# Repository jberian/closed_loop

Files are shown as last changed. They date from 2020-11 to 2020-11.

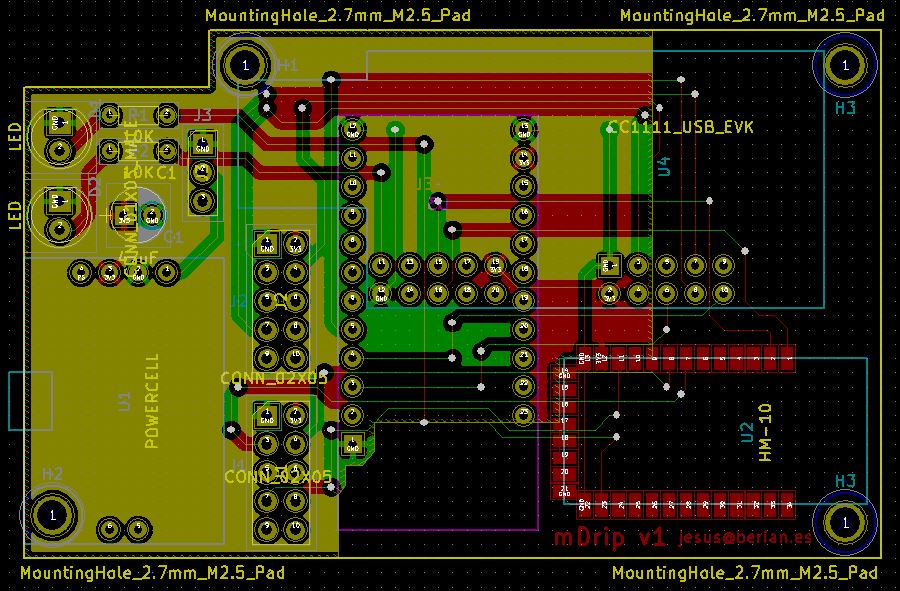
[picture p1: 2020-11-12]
Platform/Prototype/mDrip-BB.JPG

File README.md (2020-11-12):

Closed-Loop System for Type 1 diabetes
====

    This repository contains all the projects needed to build a 
    wearable closed-loop system for type 1 diabetes that uses a new
    algorithm to estimate the basal insulin needs of the patient and
    perform the control using temporary basal rates.

## Disclaimer

    This software and information is designed for educational purposes only 
    and should NEVER be used on real patients.
    
    This information is provided 'as is' and in no event shall the 
    provider be liable for any damages, including, without 
    limitation, damages resulting from lost data or lost profits or 
    revenue, the costs of recovering such data, the costs of substitute 
    data, claims by third parties or for other similar costs, or any 
    special, incidental, or consequential damages arising out of use or
    misuse of this data. The accuracy or reliability of the data is not 
    guaranteed or warranted in any way and the provider disclaim 
    liability of any kind whatsoever, including, without limitation, 
    liability for quality, performance, merchantability and fitness 
    for a particular purpose arising out of the use, or inability 
    to use the data. Information obtained via this software MUST
    NEVER BE USED to take medical decisions.

## [License - GPL V2](gpl-v2)
[gpl-2]: https://www.gnu.org/licenses/old-licenses/gpl-2.0.txt

    This program is free software: you can redistribute it and/or modify
    it under the terms of the GNU General Public License as published by
    the Free Software Foundation version 2 of the License.

    This program is distributed in the hope that it will be useful,
    but WITHOUT ANY WARRANTY; without even the implied warranty of
    MERCHANTABILITY or FITNESS FOR A PARTICULAR PURPOSE.  See the
    GNU General Public License for more details.

    You should have received a copy of the GNU General Public License
    along with this program.  If not, see <http://www.gnu.org/licenses/>.

## Contents

   This repository containts the following information in their corresponding
   folder:
   
1. **Demo** - Contains a time-lapse video of a demo system connected to Nightscout and controlling a patient's glycaemia.

2. **Firmware** - Contains the project files needed to compile the platform's CC1111 firmware using IAR Embedded Workbench (the trial version should be enough). The code for the CC2540 processor is not included since the project should be downloaded directly from TI's website.
   
3. **Platform** - Contains the information to build two different platforms: 
    1. *Prototype* - It's a PCB in which some commercial off-the-self boards can be soldered and provides the needed interconnections for the system.
    2. *Final* - Final version of the wearable system.
 
4. **Publications** - Publications related to this work.

5. **Simulation** - Contains a modified version of the [simglucose simulator](https://github.com/jxx123/simglucose) along with a controller that behaves like the "real" version of the controller.

6. **Uploader** - Contains the xCode project for an really simple iOS uploader for Nightscout. This software allows the platform to upload data to Nightscout using an iOS device.

## Thanks

None of this would be possible without all the hard work of my colleagues Ignacio Bravo, Alfredo Gardel and Jose Luis Lazaro.

Sergio Hernandez, thank you very much for your countless hours of hardware designing.

And thank you Jinyu Xie for developing such excellent software ([simglucose](https://github.com/jxx123/simglucose)) and allow us to build upon it.

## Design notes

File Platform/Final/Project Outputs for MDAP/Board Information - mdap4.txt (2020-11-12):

Board Information Report
Filename     : D:\data\work\mdap\Altium\MDAP\mdap4.PcbDoc
Date         : 19/02/2015
Time         : 20:14:05
Time Elapsed : 00:00:00

Routing Information
    Routing completion, 100,00%
    Connections, 347
    Connections routed, 347
    Connections remaining, 0
count : 4

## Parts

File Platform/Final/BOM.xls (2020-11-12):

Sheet: Hoja1
 |  |  | farnell |  |  |  |  |  | rs |  | pn |  |  | Prec.unit
Part | cc2510.SchDoc | A200 |  | * | * | * | * | * |  | * | * | * | * | 0
Part | CC2540.SchDoc | A300 |  | * | * | * | * | * |  | * | * | * | * | 0
Part | cc1110.SchDoc | C100 | 2426879 | Re-released for DXP Platform. | Radial Cap, Thru-Hole; 2 Leads; 0.3 in Pin Spacing | RAD-0.3 | 2000-06-08 | Altium Limited | 624-2941 | 220pF | * | * | * | 0.0338
Part | cc1110.SchDoc | C101 | 2426879 | Re-released for DXP Platform. | Radial Cap, Thru-Hole; 2 Leads; 0.3 in Pin Spacing | RAD-0.3 | 2000-06-08 | Altium Limited | 624-2941 | 220pF | * | * | * | 0.0338
Part | cc1110.SchDoc | C102 | 1865457 | Re-released for DXP Platform. | Radial Cap, Thru-Hole; 2 Leads; 0.3 in Pin Spacing | RAD-0.3 | 2000-06-08 | Altium Limited | 788-2843 | 100nF | * | * | * | 0.0126
Part | cc1110.SchDoc | C103 | 1865457 | Re-released for DXP Platform. | Radial Cap, Thru-Hole; 2 Leads; 0.3 in Pin Spacing | RAD-0.3 | 2000-06-08 | Altium Limited | 788-2843 | 100nF | * | * | * | 0.0126
Part | cc1110.SchDoc | C104 | 1865457 | Re-released for DXP Platform. | Radial Cap, Thru-Hole; 2 Leads; 0.3 in Pin Spacing | RAD-0.3 | 2000-06-08 | Altium Limited | 788-2843 | 100nF | * | * | * | 0.0126
Part | cc1110.SchDoc | C105 | 1865457 | Re-released for DXP Platform. | Radial Cap, Thru-Hole; 2 Leads; 0.3 in Pin Spacing | RAD-0.3 | 2000-06-08 | Altium Limited | 788-2843 | 100nF | * | * | * | 0.0126
Part | cc1110.SchDoc | C106 | 2426879 | Re-released for DXP Platform. | Radial Cap, Thru-Hole; 2 Leads; 0.3 in Pin Spacing | RAD-0.3 | 2000-06-08 | Altium Limited | 749-2138 | 2u2 | * | * | * | 0.0338
Part | cc1110.SchDoc | C107 | 1865457 | Re-released for DXP Platform. | Radial Cap, Thru-Hole; 2 Leads; 0.3 in Pin Spacing | RAD-0.3 | 2000-06-08 | Altium Limited | 788-2843 | 100nF | * | * | * | 0.0126
Part | cc1110.SchDoc | C108 | 2426879 | Re-released for DXP Platform. | Radial Cap, Thru-Hole; 2 Leads; 0.3 in Pin Spacing | RAD-0.3 | 2000-06-08 | Altium Limited | 749-2138 | 2u2 | * | * | * | 0.0338
Part | cc1110.SchDoc | C109 | 1865457 | Re-released for DXP Platform. | Radial Cap, Thru-Hole; 2 Leads; 0.3 in Pin Spacing | RAD-0.3 | 2000-06-08 | Altium Limited | 806-8495 | 100pF | * | * | * | 0.0126
Part | cc1110.SchDoc | C110 | 1828869 (http://es.farnell.com/murata/grm1555c1h1r5ca01d/condensador-0402-c0g-50v-1-5-pf/dp/1828869) | Re-released for DXP Platform. | Radial Cap, Thru-Hole; 2 Leads; 0.3 in Pin Spacing | RAD-0.3 | 2000-06-08 | Altium Limited | 788-0276 | 1.5pF | * | * | * | 0.0125
Part | cc1110.SchDoc | C111 | 2309011 | Re-released for DXP Platform. | Radial Cap, Thru-Hole; 2 Leads; 0.3 in Pin Spacing | RAD-0.3 | 2000-06-08 | Altium Limited | 788-0279 | 1pF | * | * | * | 0.005
Part | cc1110.SchDoc | C112 | 1865457 | Re-released for DXP Platform. | Radial Cap, Thru-Hole; 2 Leads; 0.3 in Pin Spacing | RAD-0.3 | 2000-06-08 | Altium Limited | 806-8495 | 100pF | * | * | * | 0.0126
Part | cc1110.SchDoc | C113 | 2426879 | Re-released for DXP Platform. | Radial Cap, Thru-Hole; 2 Leads; 0.3 in Pin Spacing | RAD-0.3 | 2000-06-08 | Altium Limited | 751-2049 | 3.3pF | * | * | * | 0.0338
Part | cc1110.SchDoc | C114 | 2426879 | Re-released for DXP Platform. | Radial Cap, Thru-Hole; 2 Leads; 0.3 in Pin Spacing | RAD-0.3 | 2000-06-08 | Altium Limited |  | N.M. | * | * | * | 0.0338
Part | cc1110.SchDoc | C115 | 1828869 (http://es.farnell.com/murata/grm1555c1h1r5ca01d/condensador-0402-c0g-50v-1-5-pf/dp/1828869) | Re-released for DXP Platform. | Radial Cap, Thru-Hole; 2 Leads; 0.3 in Pin Spacing | RAD-0.3 | 2000-06-08 | Altium Limited | 788-0276 | 1.5pF | * | * | * | 0.0125
Part | cc1110.SchDoc | C116 | 2218840 | Re-released for DXP Platform. | Radial Cap, Thru-Hole; 2 Leads; 0.3 in Pin Spacing | RAD-0.3 | 2000-06-08 | Altium Limited | 788-0266 | 15pF | * | * | * | 0.026
Part | cc1110.SchDoc | C117 | 2210762 | Re-released for DXP Platform. | Radial Cap, Thru-Hole; 2 Leads; 0.3 in Pin Spacing | RAD-0.3 | 2000-06-08 | Altium Limited | 788-0263 | 12pF | * | * | * | 0.0686
Part | cc1110.SchDoc | C118 | 2218840 | Re-released for DXP Platform. | Radial Cap, Thru-Hole; 2 Leads; 0.3 in Pin Spacing | RAD-0.3 | 2000-06-08 | Altium Limited | 788-0266 | 15pF | * | * | * | 0.026
Part | cc1110.SchDoc | C119 | 2210762 | Re-released for DXP Platform. | Radial Cap, Thru-Hole; 2 Leads; 0.3 in Pin Spacing | RAD-0.3 | 2000-06-08 | Altium Limited | 788-0263 | 12pF | * | * | * | 0.0686
Part | cc2510.SchDoc | C200 | 2426879 | Re-released for DXP Platform. | Radial Cap, Thru-Hole; 2 Leads; 0.3 in Pin Spacing | RAD-0.3 | 2000-06-08 | Altium Limited | 624-2941 | 220pF | * | * | * | 0.0338
Part | cc2510.SchDoc | C201 | 2426879 | Re-released for DXP Platform. | Radial Cap, Thru-Hole; 2 Leads; 0.3 in Pin Spacing | RAD-0.3 | 2000-06-08 | Altium Limited | 624-2941 | 220pF | * | * | * | 0.0338
Part | cc2510.SchDoc | C202 | 1865457 | Re-released for DXP Platform. | Radial Cap, Thru-Hole; 2 Leads; 0.3 in Pin Spacing | RAD-0.3 | 2000-06-08 | Altium Limited | 788-2843 | 100nF | * | * | * | 0.0126
Part | cc2510.SchDoc | C203 | 1865457 | Re-released for DXP Platform. | Radial Cap, Thru-Hole; 2 Leads; 0.3 in Pin Spacing | RAD-0.3 | 2000-06-08 | Altium Limited | 788-2843 | 100nF | * | * | * | 0.0126
Part | cc2510.SchDoc | C204 | 1865457 | Re-released for DXP Platform. | Radial Cap, Thru-Hole; 2 Leads; 0.3 in Pin Spacing | RAD-0.3 | 2000-06-08 | Altium Limited | 788-2843 | 100nF | * | * | * | 0.0126
Part | cc2510.SchDoc | C205 | 1865457 | Re-released for DXP Platform. | Radial Cap, Thru-Hole; 2 Leads; 0.3 in Pin Spacing | RAD-0.3 | 2000-06-08 | Altium Limited | 788-2843 | 100nF | * | * | * | 0.0126
Part | cc2510.SchDoc | C206 | 2426879 | Re-released for DXP Platform. | Radial Cap, Thru-Hole; 2 Leads; 0.3 in Pin Spacing | RAD-0.3 | 2000-06-08 | Altium Limited | 749-2138 | 2u2 | * | * | * | 0.0338
Part | cc2510.SchDoc | C207 | 1865457 | Re-released for DXP Platform. | Radial Cap, Thru-Hole; 2 Leads; 0.3 in Pin Spacing | RAD-0.3 | 2000-06-08 | Altium Limited | 788-2843 | 100nF | * | * | * | 0.0126
Part | cc2510.SchDoc | C208 | 2426879 | Re-released for DXP Platform. | Radial Cap, Thru-Hole; 2 Leads; 0.3 in Pin Spacing | RAD-0.3 | 2000-06-08 | Altium Limited | 749-2138 | 2u2 | * | * | * | 0.0338
Part | cc2510.SchDoc | C209 | 2309011 | Re-released for DXP Platform. | Radial Cap, Thru-Hole; 2 Leads; 0.3 in Pin Spacing | RAD-0.3 | 2000-06-08 | Altium Limited | 788-0279 | 1pF | * | * | * | 0.005
Part | cc2510.SchDoc | C210 | 1865457 | Re-released for DXP Platform. | Radial Cap, Thru-Hole; 2 Leads; 0.3 in Pin Spacing | RAD-0.3 | 2000-06-08 | Altium Limited | 806-8495 | 100pF | * | * | * | 0.0126
Part | cc2510.SchDoc | C211 | 1865457 | Re-released for DXP Platform. | Radial Cap, Thru-Hole; 2 Leads; 0.3 in Pin Spacing | RAD-0.3 | 2000-06-08 | Altium Limited | 806-8495 | 100pF | * | * | * | 0.0126
Part | cc2510.SchDoc | C212 | 2309011 | Re-released for DXP Platform. | Radial Cap, Thru-Hole; 2 Leads; 0.3 in Pin Spacing | RAD-0.3 | 2000-06-08 | Altium Limited | 788-0279 | 1pF | * | * | * | 0.005
Part | cc2510.SchDoc | C213 | 1865457 | Re-released for DXP Platform. | Radial Cap, Thru-Hole; 2 Leads; 0.3 in Pin Spacing | RAD-0.3 | 2000-06-08 | Altium Limited | 755-2033 | 1.8nF | * | * | * | 0.0126
Part | cc2510.SchDoc | C214 | #N/A | Re-released for DXP Platform. | Radial Cap, Thru-Hole; 2 Leads; 0.3 in Pin Spacing | RAD-0.3 | 2000-06-08 | Altium Limited | 806-8489 | 1.5nF | * | * | * | 0.0478
Part | cc2510.SchDoc | C215 | 2218840 | Re-released for DXP Platform. | Radial Cap, Thru-Hole; 2 Leads; 0.3 in Pin Spacing | RAD-0.3 | 2000-06-08 | Altium Limited | 788-0266 | 15pF | * | * | * | 0.026
Part | cc2510.SchDoc | C216 | 2210762 | Re-released for DXP Platform. | Radial Cap, Thru-Hole; 2 Leads; 0.3 in Pin Spacing | RAD-0.3 | 2000-06-08 | Altium Limited | 788-0263 | 12pF | * | * | * | 0.0686
Part | cc2510.SchDoc | C217 | 2218840 | Re-released for DXP Platform. | Radial Cap, Thru-Hole; 2 Leads; 0.3 in Pin Spacing | RAD-0.3 | 2000-06-08 | Altium Limited | 788-0266 | 15pF | * | * | * | 0.026
Part | cc2510.SchDoc | C218 | 2210762 | Re-released for DXP Platform. | Radial Cap, Thru-Hole; 2 Leads; 0.3 in Pin Spacing | RAD-0.3 | 2000-06-08 | Altium Limited | 788-0263 | 12pF | * | * | * | 0.0686
Part | CC2540.SchDoc | C300 | 2426879 | Re-released for DXP Platform. | Radial Cap, Thru-Hole; 2 Leads; 0.3 in Pin Spacing | RAD-0.3 | 2000-06-08 | Altium Limited | 624-2238 | 47pF | * | * | * | 0.0338
Part | CC2540.SchDoc | C301 | 2426879 | Re-released for DXP Platform. | Radial Cap, Thru-Hole; 2 Leads; 0.3 in Pin Spacing | RAD-0.3 | 2000-06-08 | Altium Limited | 624-2238 | 47pF | * | * | * | 0.0338
Part | CC2540.SchDoc | C302 | 2426879 | Re-released for DXP Platform. | Radial Cap, Thru-Hole; 2 Leads; 0.3 in Pin Spacing | RAD-0.3 | 2000-06-08 | Altium Limited | 624-2941 | 220pF | * | * | * | 0.0338
Part | CC2540.SchDoc | C303 | 2426879 | Re-released for DXP Platform. | Radial Cap, Thru-Hole; 2 Leads; 0.3 in Pin Spacing | RAD-0.3 | 2000-06-08 | Altium Limited | 624-2941 | 220pF | * | * | * | 0.0338
Part | CC2540.SchDoc | C304 | 1865457 | Re-released for DXP Platform. | Radial Cap, Thru-Hole; 2 Leads; 0.3 in Pin Spacing | RAD-0.3 | 2000-06-08 | Altium Limited | 788-2843 | 100nF | * | * | * | 0.0126
Part | CC2540.SchDoc | C305 | 1865457 | Re-released for DXP Platform. | Radial Cap, Thru-Hole; 2 Leads; 0.3 in Pin Spacing | RAD-0.3 | 2000-06-08 | Altium Limited | 788-2843 | 100nF | * | * | * | 0.0126
Part | CC2540.SchDoc | C306 | 1865457 | Re-released for DXP Platform. | Radial Cap, Thru-Hole; 2 Leads; 0.3 in Pin Spacing | RAD-0.3 | 2000-06-08 | Altium Limited | 788-2843 | 100nF | * | * | * | 0.0126
Part | CC2540.SchDoc | C307 | 1865457 | Re-released for DXP Platform. | Radial Cap, Thru-Hole; 2 Leads; 0.3 in Pin Spacing | RAD-0.3 | 2000-06-08 | Altium Limited | 788-2843 | 100nF | * | * | * | 0.0126
Part | CC2540.SchDoc | C308 | 2426879 | Re-released for DXP Platform. | Radial Cap, Thru-Hole; 2 Leads; 0.3 in Pin Spacing | RAD-0.3 | 2000-06-08 | Altium Limited | 749-2138 | 2u2 | * | * | * | 0.0338
Part | CC2540.SchDoc | C309 | 2309011 | Re-released for DXP Platform. | Radial Cap, Thru-Hole; 2 Leads; 0.3 in Pin Spacing | RAD-0.3 | 2000-06-08 | Altium Limited | 788-0260 | 18pF | * | * | * | 0.005
Part | CC2540.SchDoc | C310 | 2309011 | Re-released for DXP Platform. | Radial Cap, Thru-Hole; 2 Leads; 0.3 in Pin Spacing | RAD-0.3 | 2000-06-08 | Altium Limited | 788-0279 | 1pF | * | * | * | 0.005
Part | CC2540.SchDoc | C311 | 2309011 | Re-released for DXP Platform. | Radial Cap, Thru-Hole; 2 Leads; 0.3 in Pin Spacing | RAD-0.3 | 2000-06-08 | Altium Limited | 788-0279 | 1pF | * | * | * | 0.005
Part | CC2540.SchDoc | C312 | 2309011 | Re-released for DXP Platform. | Radial Cap, Thru-Hole; 2 Leads; 0.3 in Pin Spacing | RAD-0.3 | 2000-06-08 | Altium Limited | 788-0260 | 18pF | * | * | * | 0.005
Part | CC2540.SchDoc | C313 | 2309011 | Re-released for DXP Platform. | Radial Cap, Thru-Hole; 2 Leads; 0.3 in Pin Spacing | RAD-0.3 | 2000-06-08 | Altium Limited | 788-0279 | 1pF | * | * | * | 0.005
Part | CC2540.SchDoc | C314 | 2218840 | Re-released for DXP Platform. | Radial Cap, Thru-Hole; 2 Leads; 0.3 in Pin Spacing | RAD-0.3 | 2000-06-08 | Altium Limited | 788-0266 | 15pF | * | * | * | 0.026
Part | CC2540.SchDoc | C315 | 2210762 | Re-released for DXP Platform. | Radial Cap, Thru-Hole; 2 Leads; 0.3 in Pin Spacing | RAD-0.3 | 2000-06-08 | Altium Limited | 788-0263 | 12pF | * | * | * | 0.0686
Part | CC2540.SchDoc | C316 | 2218840 | Re-released for DXP Platform. | Radial Cap, Thru-Hole; 2 Leads; 0.3 in Pin Spacing | RAD-0.3 | 2000-06-08 | Altium Limited | 788-0266 | 15pF | * | * | * | 0.026
Part | CC2540.SchDoc | C317 | 2210762 | Re-released for DXP Platform. | Radial Cap, Thru-Hole; 2 Leads; 0.3 in Pin Spacing | RAD-0.3 | 2000-06-08 | Altium Limited | 788-0263 | 12pF | * | * | * | 0.0686
Part | CC2540.SchDoc | C318 | 1865457 | Re-released for DXP Platform. | Radial Cap, Thru-Hole; 2 Leads; 0.3 in Pin Spacing | RAD-0.3 | 2000-06-08 | Altium Limited | 788-2843 | 100nF | * | * | * | 0.0126
Part | CC2540.SchDoc | C319 | 2320857 | Re-released for DXP Platform. | Radial Cap, Thru-Hole; 2 Leads; 0.3 in Pin Spacing | RAD-0.3 | 2000-06-08 | Altium Limited | 653-0490 | 1uF | * | * | * | 0.0265
Part | CC2540.SchDoc | C320 | 1865457 | Re-released for DXP Platform. | Radial Cap, Thru-Hole; 2 Leads; 0.3 in Pin Spacing | RAD-0.3 | 2000-06-08 | Altium Limited | 788-2843 | 100nF | * | * | * | 0.0126
Part | Alim.SchDoc | C400 | 1865457 | Re-released for DXP Platform. | Radial Cap, Thru-Hole; 2 Leads; 0.3 in Pin Spacing | RAD-0.3 | 2000-06-08 | Altium Limited | 788-2843 | 100nF | * | * | * | 0.0126
Part | Alim.SchDoc | C401 | 1865457 | Re-released for DXP Platform. | Radial Cap, Thru-Hole; 2 Leads; 0.3 in Pin Spacing | RAD-0.3 | 2000-06-08 | Altium Limited | 624-2301 | 10nF | * | * | * | 0.0126
Part | Alim.SchDoc | C402 | 2218840 | Re-released for DXP Platform. | Radial Cap, Thru-Hole; 2 Leads; 0.3 in Pin Spacing | RAD-0.3 | 2000-06-08 | Altium Limited | 788-0266 | 15pF | * | * | * | 0.026
Part | Alim.SchDoc | C403 | 2320857 | Re-released for DXP Platform. | Radial Cap, Thru-Hole; 2 Leads; 0.3 in Pin Spacing | RAD-0.3 | 2000-06-08 | Altium Limited | 653-0490 | 1uF | * | * | * | 0.0265
Part | Alim.SchDoc | C404 | 2426879 | Re-released for DXP Platform. | Radial Cap, Thru-Hole; 2 Leads; 0.3 in Pin Spacing | RAD-0.3 | 2000-06-08 | Altium Limited | 698-3579 | 4.7uF | * | * | * | 0.0338
Part | Alim.SchDoc | C405 | 2426879 | Re-released for DXP Platform. | Radial Cap, Thru-Hole; 2 Leads; 0.3 in Pin Spacing | RAD-0.3 | 2000-06-08 | Altium Limited | 698-3579 | 4.7uF | * | * | * | 0.0338
Part | TOP.SchDoc | D1 |  | Re-released for DXP Platform. | SM LED; 2 Flat Leads | 3.2X1.6X1.1 | 2000-06-08 | Altium Limited |  | * | * | * | * | 0.02
Part | TOP.SchDoc | D2 |  | Re-released for DXP Platform. | SM LED; 2 Flat Leads | 3.2X1.6X1.1 | 2000-06-08 | Altium Limited |  | * | * | * | * | 0.02
Part | TOP.SchDoc | D3 |  | Re-released for DXP Platform. | SM LED; 2 Flat Leads | 3.2X1.6X1.1 | 2000-06-08 | Altium Limited |  | * | * | * | * | 0.02
Part | TOP.SchDoc | D4 |  | Re-released for DXP Platform. | SM LED; 2 Flat Leads | 3.2X1.6X1.1 | 2000-06-08 | Altium Limited |  | * | * | * | * | 0.02
Part | TOP.SchDoc | D5 |  | Re-released for DXP Platform. | SM LED; 2 Flat Leads | 3.2X1.6X1.1 | 2000-06-08 | Altium Limited |  | * | * | * | * | 0.02
Part | TOP.SchDoc | D6 |  | Re-released for DXP Platform. | SM LED; 2 Flat Leads | 3.2X1.6X1.1 | 2000-06-08 | Altium Limited |  | * | * | * | * | 0.02
Part | Alim.SchDoc | D400 |  | Re-released for DXP Platform. | SM LED; 2 Flat Leads | 3.2X1.6X1.1 | 2000-06-08 | Altium Limited |  | * | * | * | * | 0.02
Part | Alim.SchDoc | D401 |  | Re-released for DXP Platform. | SM LED; 2 Flat Leads | 3.2X1.6X1.1 | 2000-06-08 | Altium Limited |  | * | * | * | * | 0.02
Part | cc1110.SchDoc | E100 | 1885493 | Re-released for DXP Platform. | * | PIN1 | 1999-03-24 | Altium Limited | N.E. | * | 0868AT43A0020E | * | * | 1.12
Part | TOP.SchDoc | J1 | Smart | * | * | 440247 | 2004-07-15 | Altium Limited |  | * | * | * | * | 0.2
Part | cc1110.SchDoc | L100 | 1669624 | IPC-7351 Footprint Added. | Chip Inductor | 0402-A | 2000-06-08 | Altium Limited | 777-6861 | 102 | * | 1005 | 402 | 0.0643
Part | cc1110.SchDoc | L101 | 2103101 | IPC-7351 Footprint Added. | Chip Inductor | 0402-A | 2000-06-08 | Altium Limited | 777-7022 | 18nH | * | 1005 | 402 | 0.0439
Part | cc1110.SchDoc | L102 | 2103098 | IPC-7351 Footprint Added. | Chip Inductor | 0402-A | 2000-06-08 | Altium Limited | 701-6910 | 12nH | * | 1005 | 402 | 0.045
Part | cc1110.SchDoc | L103 | 2103098 | IPC-7351 Footprint Added. | Chip Inductor | 0402-A | 2000-06-08 | Altium Limited | 701-6910 | 12nH | * | 1005 | 402 | 0.045
Part | cc1110.SchDoc | L104 | 2103098 | IPC-7351 Footprint Added. | Chip Inductor | 0402-A | 2000-06-08 | Altium Limited | 701-6910 | 12nH | * | 1005 | 402 | 0.045
Part | cc1110.SchDoc | L105 | 1669627 | IPC-7351 Footprint Added. | Chip Inductor | 0402-A | 2000-06-08 | Altium Limited | 701-6807 | 1.8nH | * | 1005 | 402 | 0.0634
Part | cc1110.SchDoc | L106 | 2103098 | IPC-7351 Footprint Added. | Chip Inductor | 0402-A | 2000-06-08 | Altium Limited | 701-6910 | 12nH | * | 1005 | 402 | 0.045
Part | cc1110.SchDoc | L107 | 2103101 | IPC-7351 Footprint Added. | Chip Inductor | 0402-A | 2000-06-08 | Altium Limited | 777-7022 | 18nH | * | 1005 | 402 | 0.0439
Part | cc1110.SchDoc | L108 | 2103098 | IPC-7351 Footprint Added. | Chip Inductor | 0402-A | 2000-06-08 | Altium Limited | 701-6910 | 12nH | * | 1005 | 402 | 0.045
Part | cc2510.SchDoc | L200 | 1669624 | IPC-7351 Footprint Added. | Chip Inductor | 0402-A | 2000-06-08 | Altium Limited | 777-6861 | 102 | * | 1005 | 402 | 0.0643
Part | cc2510.SchDoc | L201 | 1704133 | IPC-7351 Footprint Added. | Chip Inductor | 0402-A | 2000-06-08 | Altium Limited | 701-6784 | 1.2nH | * | 1005 | 402 | 0.0822
Part | cc2510.SchDoc | L202 | 1704133 | IPC-7351 Footprint Added. | Chip Inductor | 0402-A | 2000-06-08 | Altium Limited | 701-6784 | 1.2nH | * | 1005 | 402 | 0.0822
Part | cc2510.SchDoc | L203 | 1704133 | IPC-7351 Footprint Added. | Chip Inductor | 0402-A | 2000-06-08 | Altium Limited | 701-6784 | 1.2nH | * | 1005 | 402 | 0.0822
Part | CC2540.SchDoc | L300 | 1669624 | IPC-7351 Footprint Added. | Chip Inductor | 0402-A | 2000-06-08 | Altium Limited | 777-6861 | 102 | * | 1005 | 402 | 0.0643
Part | CC2540.SchDoc | L301 | 2103067 | IPC-7351 Footprint Added. | Chip Inductor | 0402-A | 2000-06-08 | Altium Limited | 777-6978 | 2nH | * | 1005 | 402 | 0.0424
Part | CC2540.SchDoc | L302 | 1669624 | IPC-7351 Footprint Added. | Chip Inductor | 0402-A | 2000-06-08 | Altium Limited | 777-6861 | 1nH | * | 1005 | 402 | 0.0643
Part | CC2540.SchDoc | L303 | 2103077 | IPC-7351 Footprint Added. | Chip Inductor | 0402-A | 2000-06-08 | Altium Limited | 777-6987 | 3nH | * | 1005 | 402 | 0.0418
Part | CC2540.SchDoc | L304 | 2103067 | IPC-7351 Footprint Added. | Chip Inductor | 0402-A | 2000-06-08 | Altium Limited | 777-6978 | 2nH | * | 1005 | 402 | 0.0424
Part | TOP.SchDoc | P1 | Smart | Re-released for DXP Platform. | * | * | * | Altium Limited |  | * | * | * | * | 0.06
Part | TOP.SchDoc | P2 | Smart | Re-released for DXP Platform. | * | * | * | Altium Limited |  | * | * | * | * | 0.06
Part | TOP.SchDoc | P3 | Smart | Re-released for DXP Platform. | * | * | * | Altium Limited |  | * | * | * | * | 0.06
Part | Alim.SchDoc | P400 | Smart | Re-released for DXP Platform. | * | * | * | Altium Limited |  | * | * | * | * | 0.06
Part | TOP.SchDoc | R1 |  | IPC-7351 Footprint Added. | Chip Resistor | J1-0603 | 2000-06-08 | Altium Limited |  | N.M. | * | * | * | 0
Part | TOP.SchDoc | R2 | 2331719 | IPC-7351 Footprint Added. | Chip Resistor | J1-0603 | 2000-06-08 | Altium Limited | 721-7292 | 270 | * | * | * | 0.01
Part | TOP.SchDoc | R3 | 2331719 | IPC-7351 Footprint Added. | Chip Resistor | J1-0603 | 2000-06-08 | Altium Limited | 721-7292 | 270 | * | * | * | 0.01
Part | TOP.SchDoc | R4 | 2331719 | IPC-7351 Footprint Added. | Chip Resistor | J1-0603 | 2000-06-08 | Altium Limited | 721-7292 | 270 | * | * | * | 0.01
Part | TOP.SchDoc | R5 | 2331719 | IPC-7351 Footprint Added. | Chip Resistor | J1-0603 | 2000-06-08 | Altium Limited | 721-7292 | 270 | * | * | * | 0.01
Part | TOP.SchDoc | R6 |  | IPC-7351 Footprint Added. | Chip Resistor | J1-0603 | 2000-06-08 | Altium Limited |  | N.M. | * | * | * | 0
Part | TOP.SchDoc | R7 |  | IPC-7351 Footprint Added. | Chip Resistor | J1-0603 | 2000-06-08 | Altium Limited |  | N.M. | * | * | * | 0
Part | TOP.SchDoc | R8 | 2331719 | IPC-7351 Footprint Added. | Chip Resistor | J1-0603 | 2000-06-08 | Altium Limited | 721-7292 | 270 | * | * | * | 0.01
Part | TOP.SchDoc | R9 | 2331719 | IPC-7351 Footprint Added. | Chip Resistor | J1-0603 | 2000-06-08 | Altium Limited | 721-7292 | 270 | * | * | * | 0.01
Part | TOP.SchDoc | R10 | 2331749 | IPC-7351 Footprint Added. | Chip Resistor | J1-0603 | 2000-06-08 | Altium Limited | N.E. | 47K | * | * | * | 0.01
Part | TOP.SchDoc | R11 | 2331749 | IPC-7351 Footprint Added. | Chip Resistor | J1-0603 | 2000-06-08 | Altium Limited | N.E. | 47K | * | * | * | 0.01
Part | cc1110.SchDoc | R100 | 2333520 | IPC-7351 Footprint Added. | Chip Resistor | J1-0603 | 2000-06-08 | Altium Limited | N.E. | 10K | * | * | * | 0.0099
Part | cc1110.SchDoc | R101 | 2331750 | IPC-7351 Footprint Added. | Chip Resistor | J1-0603 | 2000-06-08 | Altium Limited | N.E. | 56K | * | * | * | 0.01
Part | cc2510.SchDoc | R200 | 2333520 | IPC-7351 Footprint Added. | Chip Resistor | J1-0603 | 2000-06-08 | Altium Limited | N.E. | 10K | * | * | * | 0.0099
Part | cc2510.SchDoc | R202 | 2331750 | IPC-7351 Footprint Added. | Chip Resistor | J1-0603 | 2000-06-08 | Altium Limited | N.E. | 56K | * | * | * | 0.01
Part | CC2540.SchDoc | R300 | 2333520 | IPC-7351 Footprint Added. | Chip Resistor | J1-0603 | 2000-06-08 | Altium Limited | N.E. | 10K | * | * | * | 0.0099
Part | CC2540.SchDoc | R301 | 2333563 | IPC-7351 Footprint Added. | Chip Resistor | J1-0603 | 2000-06-08 | Altium Limited | N.E. | 1K5 | * | * | * | 0.0099
Part | CC2540.SchDoc | R302 | 2331705 | IPC-7351 Footprint Added. | Chip Resistor | J1-0603 | 2000-06-08 | Altium Limited | 721-7227 | 33 | * | * | * | 0.01
Part | CC2540.SchDoc | R303 | 2331705 | IPC-7351 Footprint Added. | Chip Resistor | J1-0603 | 2000-06-08 | Altium Limited | 721-7227 | 33 | * | * | * | 0.01
Part | CC2540.SchDoc | R305 | 2331750 | IPC-7351 Footprint Added. | Chip Resistor | J1-0603 | 2000-06-08 | Altium Limited | N.E. | 56K | * | * | * | 0.01
Part | Alim.SchDoc | R400 | 2333563 | IPC-7351 Footprint Added. | Chip Resistor | J1-0603 | 2000-06-08 | Altium Limited | N.E. | 1K5 | * | * | * | 0.0099
Part | Alim.SchDoc | R401 | 2331753 | IPC-7351 Footprint Added. | Chip Resistor | J1-0603 | 2000-06-08 | Altium Limited | N.E. | 100K | * | * | * | 0.0099
Part | Alim.SchDoc | R402 | 2333563 | IPC-7351 Footprint Added. | Chip Resistor | J1-0603 | 2000-06-08 | Altium Limited | N.E. | 1K5 | * | * | * | 0.0099
Part | Alim.SchDoc | R403 | 2331753 | IPC-7351 Footprint Added. | Chip Resistor | J1-0603 | 2000-06-08 | Altium Limited | N.E. | 100K | * | * | * | 0.0099
Part | Alim.SchDoc | R404 | 2309111 | IPC-7351 Footprint Added. | Chip Resistor | J1-0603 | 2000-06-08 | Altium Limited | 740-8870 | 0R | * | * | * | 0.005
Part | Alim.SchDoc | R405 |  | IPC-7351 Footprint Added. | Chip Resistor | J1-0603 | 2000-06-08 | Altium Limited |  | N.M. | * | * | * | 0
Part | Alim.SchDoc | R406 | 1785891 | IPC-7351 Footprint Added. | Chip Resistor | J1-0603 | 2000-06-08 | Altium Limited | N.E. | 44K2 | * | * | * | 0.056
Part | Alim.SchDoc | R407 |  | IPC-7351 Footprint Added. | Chip Resistor | J1-0603 | 2000-06-08 | Altium Limited |  | N.M. | * | * | * | 0
Part | Alim.SchDoc | R408 | 1527635 | IPC-7351 Footprint Added. | Chip Resistor | J1-0603 | 2000-06-08 | Altium Limited | N.E. | 30K1 | * | * | * | 0.0461
Part | Alim.SchDoc | R409 | 2333520 | IPC-7351 Footprint Added. | Chip Resistor | J1-0603 | 2000-06-08 | Altium Limited | N.E. | 10K | * | * | * | 0.0099
Part | Alim.SchDoc | R410 | 2116731 | IPC-7351 Footprint Added. | Chip Resistor | J1-0603 | 2000-06-08 | Altium Limited | N.E. | 3K06 | * | * | * | 0.186
Part | Alim.SchDoc | R411 | 2116703 | IPC-7351 Footprint Added. | Chip Resistor | J1-0603 | 2000-06-08 | Altium Limited | N.E. | 1K74 | * | * | * | 0.258
Part | Alim.SchDoc | R412 |  | IPC-7351 Footprint Added. | Chip Resistor | J1-0603 | 2000-06-08 | Altium Limited |  | N.M. | * | * | * | 0
Part | Alim.SchDoc | R413 | 2309111 | IPC-7351 Footprint Added. | Chip Resistor | J1-0603 | 2000-06-08 | Altium Limited | 740-8870 | 0R | * | * | * | 0.005
Part | cc1110.SchDoc | U100 | 2422916 | * | * | * | * | * | 459-342 | * | CC1110F32RHHR | * | * | 5
Part | cc2510.SchDoc | U200 | 1549254 | * | * | * | * | * | 459-540 | * | CC2510F16RSP | * | * | 4.46
Part | CC2540.SchDoc | U300 | 1862837RL | * | * | * | * | * | 730-0534 | * | CC2540F256RHAT | * | * | 4.42
Part | Alim.SchDoc | U400 | 2383064 | * | 16-Pin Plastic Quad Flat No-Lead, 3 x 3 mm Body, 0.5 mm Pitch, 1.7 x 1.7 mm Exposed Pad | RGT16-1700X1700TP | * | * | N.E. | * | * | * | * | 2.96
Part | Alim.SchDoc | U401 | 1460960 | * | * | * | * | * | 661-4478 | * | TPS79301DBVR | * | * | 0.832
Part | cc1110.SchDoc | Y100 | Smart | Re-released for DXP Platform. | Crystal, Thru-Hole; 2 Leads; Body 3.1 x 8.2 mm (Dia.xH) | R38 | 2000-06-08 | Altium Limited |  | * | * | * | * | 0.36
Part | cc1110.SchDoc | Y101 | Smart | Re-released for DXP Platform. | Crystal, Thru-Hole; 2 Leads; Body 3.1 x 8.2 mm (Dia.xH) | R38 | 2000-06-08 | Altium Limited |  | * | * | * | * | 0.36
Part | cc2510.SchDoc | Y200 | Smart | Re-released for DXP Platform. | Crystal, Thru-Hole; 2 Leads; Body 3.1 x 8.2 mm (Dia.xH) | R38 | 2000-06-08 | Altium Limited |  | * | * | * | * | 0.36
Part | cc2510.SchDoc | Y201 | Smart | Re-released for DXP Platform. | Crystal, Thru-Hole; 2 Leads; Body 3.1 x 8.2 mm (Dia.xH) | R38 | 2000-06-08 | Altium Limited |  | * | * | * | * | 0.36
Part | CC2540.SchDoc | Y300 | Smart | Re-released for DXP Platform. | Crystal, Thru-Hole; 2 Leads; Body 3.1 x 8.2 mm (Dia.xH) | R38 | 2000-06-08 | Altium Limited |  | * | * | * | * | 0.36
Part | CC2540.SchDoc | Y301 | Smart | Re-released for DXP Platform. | Crystal, Thru-Hole; 2 Leads; Body 3.1 x 8.2 mm (Dia.xH) | R38 | 2000-06-08 | Altium Limited |  | * | * | * | * | 0.36
 |  |  |  |  |  |  |  |  |  |  |  |  |  | 24.9576
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

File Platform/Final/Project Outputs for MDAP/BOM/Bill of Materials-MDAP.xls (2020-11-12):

Quantity | Description | Value | PN | Designator | Footprint | Manufacturer | Order N | FARNELL | SP
2 | Antenna single ended IIFA, 2450 MHz |  |  | A1, A2 | antenna_IIFA_1
6 | Capacitor | 12pF |  | C1, C4, C32, C55, C60, C61 | 0402 | FARNELL | 2210762 | 2210762
2 | Capacitor | 4.7uF |  | C2, C8 | C0805 | FARNELL | 1759414 | 1759414
7 | Capacitor | 15pF |  | C3, C5, C9, C30, C50, C59, C62 | 0402 | FARNELL | 2218840 | 2218840
6 | Capacitor | 220pF |  | C6, C21, C39, C48, C63, C64 | 0402 | FARNELL | 2426879 | 2426879
1 | Capacitor | 10nF |  | C7 | 0402 | FARNELL | 1650807 | 1650807
4 | Capacitor | 100pF |  | C10, C19, C57, C58 | 0402 | FARNELL | 2426878 | 2426878
18 | Capacitor | 100nF |  | C11, C13, C20, C22, C24, C25, C28, C33, C35, C36, C38, C40, C47, C49, C51, C52, C54, C56 | 0402 | FARNELL | 2309011 | 2309011
1 | Capacitor | 3.3pF |  | C12 | 0402 | FARNELL | 2210780 | 2210780
6 | Capacitor | 1pF |  | C14, C41, C42, C46, C65, C66 | 0402 | FARNELL | 1611944 | 1611944
2 | Capacitor | 1.5pF |  | C15, C18 | 0402 | FARNELL | 1828869 | 1828869
3 | Capacitor | 1uF |  | C16, C23, C34 | C0805 | FARNELL | 2320857 | 2320857
1 | Capacitor | N.M. |  | C17 | 0402
5 | Capacitor | 2u2 |  | C26, C29, C37, C44, C53 | C0805 | FARNELL | 1759416 | 1759416
2 | Capacitor | 47pF |  | C27, C31 | 0402 | FARNELL | 1758959 | 1758959
2 | Capacitor | 18pF |  | C43, C45 | 0402 | FARNELL | 1758947 | 1758947
1 | Capacitor | 1.8nF |  | C67 | 0402 | FARNELL | 1865457 | 1865457
1 | Capacitor | 1.5nF |  | C68 | 0402 | FARNELL | 2210797 | 2210797
4 | Typical RED, GREEN, YELLOW, AMBER GaAs LED | Rojo |  | D1, D3, D5, D7 | led_0805 | Smart Prototyping | SP-C2286 | 2099236 | SP-C2286
4 | Typical RED, GREEN, YELLOW, AMBER GaAs LED | Verde |  | D2, D4, D6, D8 | led_0805 | Smart Prototyping | SP-C2292 | 2290331 | SP-C2292
1 | Generic Antenna |  | 0868AT43A0020E | E1 | Johanson_0868AT43A0020 | FARNELL | 1885493 | 1885493
1 | USB 2.0, Right Angle, SMT, B Type, Receptacle, 5 Position, Black |  |  | J1 | USB_C10418 | Smart Prototyping | SP-C10418 |  | SP-C10418
2 | Inductor | 18nH |  | L1, L6 | 0402-A | FARNELL | 2103101 | 2103101
5 | Inductor | 12nH |  | L2, L3, L4, L5, L8 | 0402-A | FARNELL | 2103098 | 2103098
1 | Inductor | 1.8nH |  | L7 | 0402-A | FARNELL | 1669627 | 1669627
4 | Inductor | 102, 102, 1nH, 102 |  | L9, L10, L13, L15 | 0402-A | FARNELL | 1669624 | 1669624
2 | Inductor | 2nH |  | L11, L14 | 0402-A | FARNELL | 2103067 | 2103067
1 | Inductor | 3nH |  | L12 | 0402-A | FARNELL | 2103077 | 2103077
3 | Inductor | 1.2nH |  | L16, L17, L18 | 0402-A | FARNELL | 1704133 | 1704133
3 | Header, 5-Pin, Dual row |  |  | P1, P2, P3 | stl21 | Smart Prototyping | SP-C12650 |  | SP-C12650
1 | Header, 2-Pin |  |  | P4 | MOLEX_5268-2 | FARNELL | 9979611 | 9979611
4 | Resistor | 10K |  | R1, R12, R30, R32 | J1-0603 | FARNELL | 2333520 | 2333520
6 | Resistor | 270 |  | R2, R9, R25, R27, R35, R36 | J1-0603 | FARNELL | 2331719 | 2331719
3 | Resistor | 1K5 |  | R3, R4, R23 | J1-0603 | FARNELL | 2331729 | 2331729
4 | Resistor | 100K |  | R5, R13, R16, R34 | J1-0603 | FARNELL | 2331753 | 2331753
2 | Resistor | 0R |  | R6, R10 | J1-0603 | FARNELL | 2309106 | 2309106
7 | Resistor | N.M., N.M., N.M., N.M., N.M., 0R N.M., N.M. |  | R7, R8, R11, R19, R29, R33, R37 | J1-0603 |  |  | [NoValue], [NoValue], [NoValue], [NoValue], [NoValue], 2309106, [NoValue]
1 | Resistor | 3K06 |  | R14 | J1-0603 | FARNELL | 1527525 | 1527525
1 | Resistor | 1K74 |  | R15 | J1-0603 | FARNELL | 2116703 | 2116703
1 | Resistor | 30K1 |  | R17 | J1-0603 | FARNELL | 1527635 | 1527635
1 | Resistor | 44K2 |  | R18 | J1-0603 | FARNELL | 1785891 | 1785891
3 | Resistor | 56K |  | R20, R28, R31 | J1-0603 | FARNELL | 2331750 | 2331750
2 | Resistor | 47K |  | R21, R22 | J1-0603 | FARNELL | 2331749 | 2331749
2 | Resistor | 33 |  | R24, R26 | J1-0603 | FARNELL | 2331705 | 2331705
1 | Switch |  |  | S1 | puls_C3682 | Smart Prototyping | SP-C3682 |  | SP-C3682
1 | USB Friendly 0.5 A Li+ Charger with Dynamic Power Management, 10.5 V OVP, 4.3 V, -40 to 85 degC, 16-pin QFN (RGT), Green (RoHS & no Sb/Br) |  | BQ24232RGTT | U1 | RGT16-1700X1700TP_SP | FARNELL | 2383064 | 2383064
1 | Single chip transceiver |  | CC1110F32RHHR | U2 | QLP36_4_4 (Reflow) | FARNELL | 2422916 | 2422916
1 |  |  | TPS79301DBVR | U3 | SOT26A-6M | FARNELL | 1460960 | 1460960
1 | Push Button On/Off Controller |  | LTC2950CDDB-1 | U4 | DDB8 | FARNELL | 1673537 | 1673537
1 | Single chip BLE |  | CC2540F256RHAT | U5 | QFN40_RHA (DATASHEET) | FARNELL | 1862837RL | 1862837RL
1 | Single chip transceiver |  | CC2510F16RSP | U6 | QLP36_4_4 norteam silk (Reflow) | FARNELL | 1549254 | 1549254
3 | Crystal Oscillator | 32.768KHz |  | Y1, Y3, Y6 | xtal_3215 | Smart Prototyping | SP-C14473 | 2449398 | SP-C14473
2 | Crystal Oscillator | 26MHz |  | Y2, Y5 | xtal_3225 | Smart Prototyping | SP-C23363 | 2101340 | SP-C23363
1 | Crystal Oscillator | 32MHz |  | Y4 | xtal_3225 | Smart Prototyping | SP-C9009 | 1842072 | SP-C9009

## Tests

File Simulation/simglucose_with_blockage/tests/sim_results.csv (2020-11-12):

Time | BG | CGM | CHO | insulin | LBGI | HBGI | Risk
2018-01-01 00:00:00 | 149.01999999999998 | 165.79394936879046 | 0.0 | 0.013933333333333336 | 0.0 | 2.7552758979034984 | 2.7552758979034984
2018-01-01 00:03:00 | 149.01999999999927 | 161.58202232204692 | 0.0 | 0.013933333333333336 | 0.0 | 2.7552758979034135 | 2.7552758979034135
2018-01-01 00:06:00 | 149.02000000029878 | 159.2393732466224 | 0.0 | 0.013933333333333336 | 0.0 | 2.755275897942923 | 2.755275897942923
2018-01-01 00:09:00 | 149.02000000371402 | 157.4727095103013 | 0.0 | 0.013933333333333336 | 0.0 | 2.755275898393481 | 2.755275898393481
2018-01-01 00:12:00 | 149.02000002022484 | 156.10895023557376 | 0.0 | 0.013933333333333336 | 0.0 | 2.755275900571683 | 2.755275900571683
2018-01-01 00:15:00 | 149.02000007188911 | 154.97501455537622 | 0.0 | 0.013933333333333336 | 0.0 | 2.755275907387526 | 2.755275907387526
2018-01-01 00:18:00 | 149.0200001965216 | 153.89782161722894 | 0.0 | 0.013933333333333336 | 0.0 | 2.755275923829774 | 2.755275923829774
2018-01-01 00:21:00 | 149.02000044982267 | 152.704290585888 | 0.0 | 0.013933333333333336 | 0.0 | 2.7552759572467305 | 2.7552759572467305
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

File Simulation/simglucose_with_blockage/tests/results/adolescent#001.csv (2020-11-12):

Time | BG | CGM | CHO | insulin | LBGI | HBGI | Risk
2019-03-18 00:00:00 | 149.01999999999998 | 165.79394936879046 | 0.0 | 0.013933333333333336 | 0.0 | 2.7552758979034984 | 2.7552758979034984
2019-03-18 00:03:00 | 149.01999999999927 | 161.58202232204692 | 0.0 | 0.013933333333333336 | 0.0 | 2.7552758979034135 | 2.7552758979034135
2019-03-18 00:06:00 | 149.02000000029878 | 159.2393732466224 | 0.0 | 0.013933333333333336 | 0.0 | 2.755275897942923 | 2.755275897942923
2019-03-18 00:09:00 | 149.02000000371402 | 157.4727095103013 | 0.0 | 0.013933333333333336 | 0.0 | 2.755275898393481 | 2.755275898393481
2019-03-18 00:12:00 | 149.02000002022484 | 156.10895023557376 | 0.0 | 0.013933333333333336 | 0.0 | 2.755275900571683 | 2.755275900571683
2019-03-18 00:15:00 | 149.02000007188911 | 154.97501455537622 | 0.0 | 0.013933333333333336 | 0.0 | 2.755275907387526 | 2.755275907387526
2019-03-18 00:18:00 | 149.0200001965216 | 153.89782161722894 | 0.0 | 0.013933333333333336 | 0.0 | 2.755275923829774 | 2.755275923829774
2019-03-18 00:21:00 | 149.02000044982267 | 152.704290585888 | 0.0 | 0.013933333333333336 | 0.0 | 2.7552759572467305 | 2.7552759572467305
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

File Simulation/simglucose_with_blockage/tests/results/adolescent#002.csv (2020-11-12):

Time | BG | CGM | CHO | insulin | LBGI | HBGI | Risk
2019-03-18 06:00:00 | 152.41 | 169.18394936879048 | 0.0 | 0.015300000000000001 | 0.0 | 3.2153271698947945 | 3.2153271698947945
2019-03-18 06:03:00 | 152.40999999999667 | 164.9720223220426 | 0.0 | 0.015300000000000001 | 0.0 | 3.215327169894323 | 3.215327169894323
2019-03-18 06:06:00 | 152.40999999970674 | 162.62937324620282 | 0.0 | 0.015300000000000001 | 0.0 | 3.215327169853907 | 3.215327169853907
2019-03-18 06:09:00 | 152.4099999968922 | 160.86270950565336 | 0.0 | 0.015300000000000001 | 0.0 | 3.2153271694615904 | 3.2153271694615904
2019-03-18 06:12:00 | 152.40999998483042 | 159.498950210372 | 0.0 | 0.015300000000000001 | 0.0 | 3.215327167780181 | 3.215327167780181
2019-03-18 06:15:00 | 152.40999995096405 | 158.36501446488685 | 0.0 | 0.015300000000000001 | 0.0 | 3.215327163059307 | 3.215327163059307
2019-03-18 06:18:00 | 152.40999987690464 | 157.28782136784247 | 0.0 | 0.015300000000000001 | 0.0 | 3.2153271527356204 | 3.2153271527356204
2019-03-18 06:21:00 | 152.4099997391752 | 156.094290012522 | 0.0 | 0.015300000000000001 | 0.0 | 3.21532713353651 | 3.21532713353651
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

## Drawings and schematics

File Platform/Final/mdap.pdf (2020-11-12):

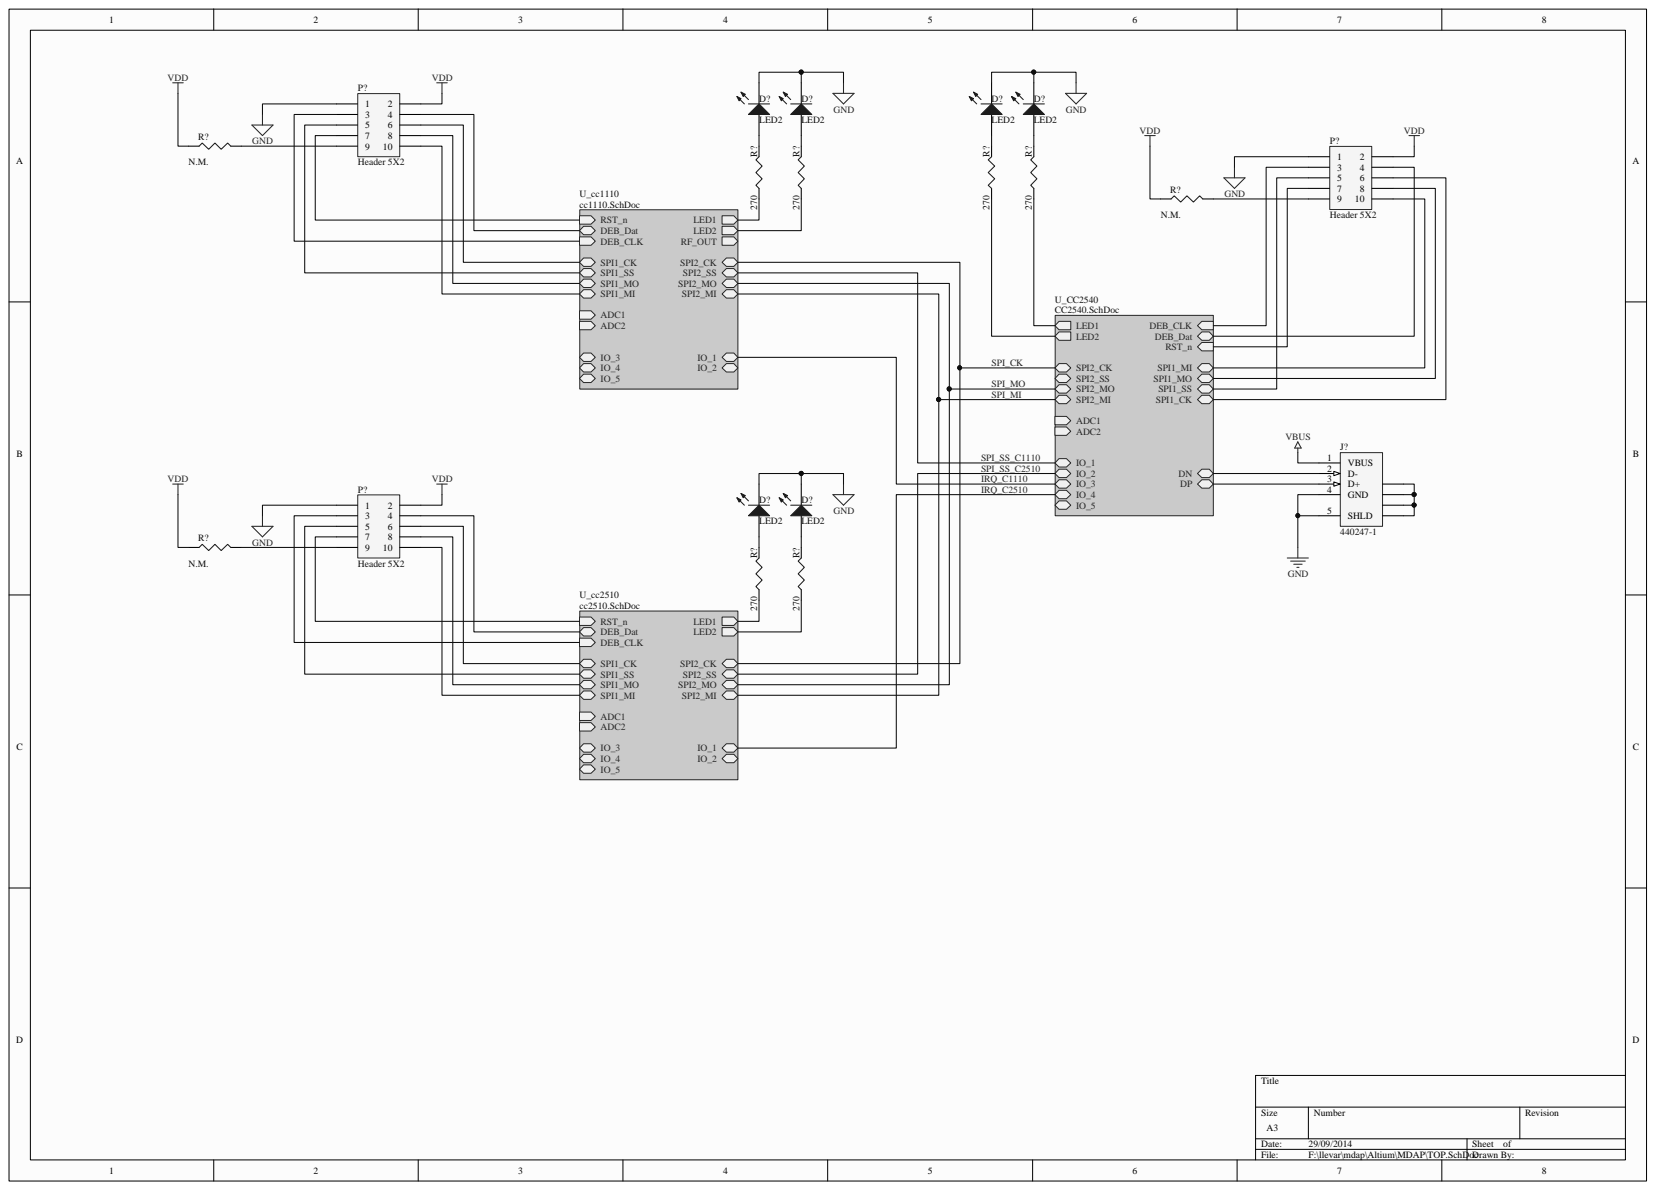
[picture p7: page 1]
Title; Size; Number; Revision; Date:; Sheet of; File:; F:\llevar\mdap\Altium\MDAP\TOP.SchDocDrawn By:; DEB_Dat DEB_CLK; RST_n; SPI1_MI; SPI1_MO; SPI1_SS; SPI1_CK; SPI2_CK; SPI2_SS SPI2_MO SPI2_MI; LED1 LED2 RF_OUT; ADC1 ADC2; U_cc1110 cc1110.SchDoc; LED1 LED2; U_cc2510 cc2510.SchDoc; Header 5X2; VDD; GND; LED2; DEB_Dat; DEB_CLK; SPI1_MI SPI1_MO SPI1_SS SPI1_CK; SPI2_CK SPI2_SS SPI2_MO SPI2_MI; U_CC2540 CC2540.SchDoc; SPI_CK; SPI_MO SPI_MI; SPI_SS_C1110 SPI_SS_C2510 IRQ_C1110 IRQ_C2510; VBUS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

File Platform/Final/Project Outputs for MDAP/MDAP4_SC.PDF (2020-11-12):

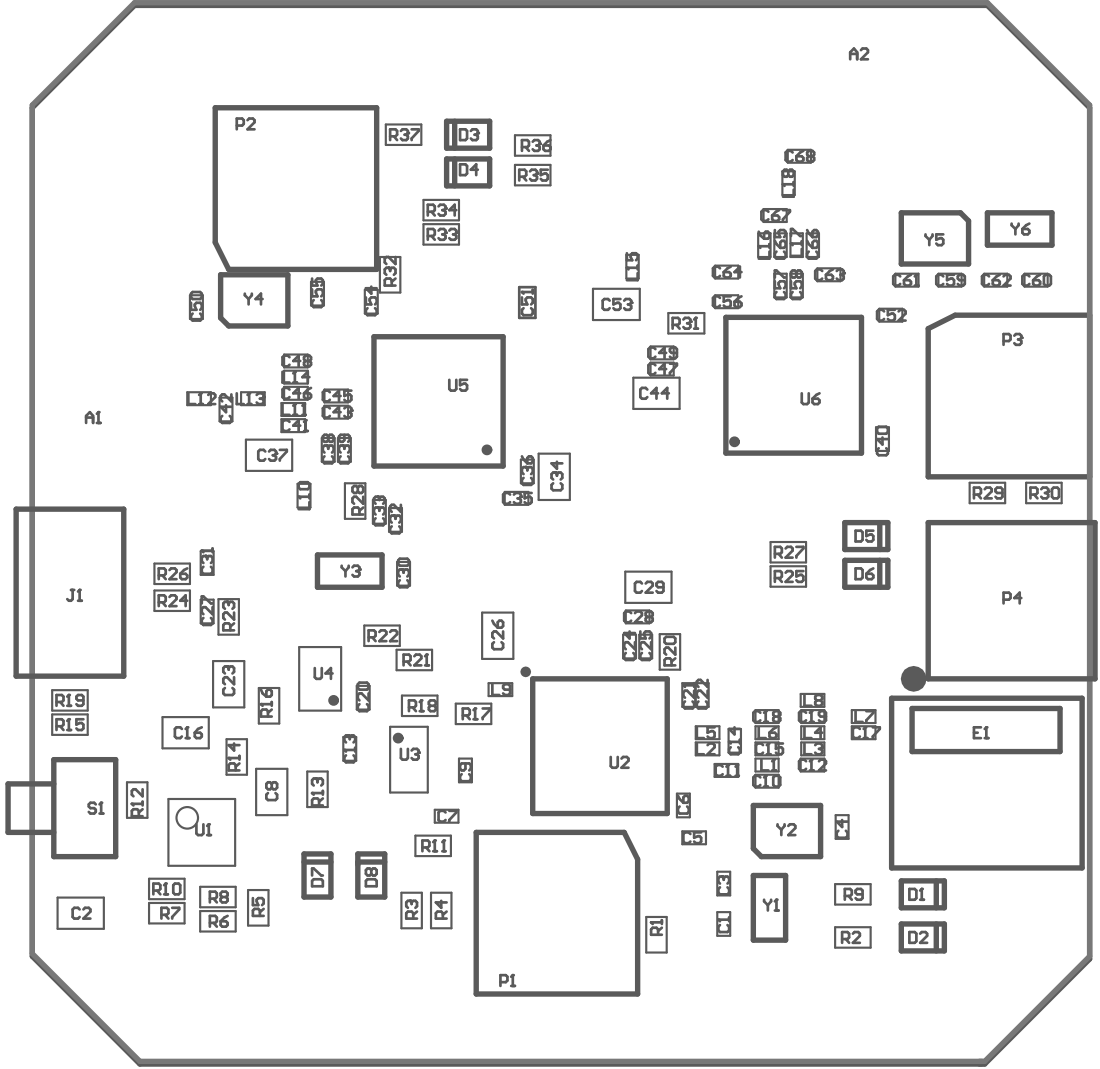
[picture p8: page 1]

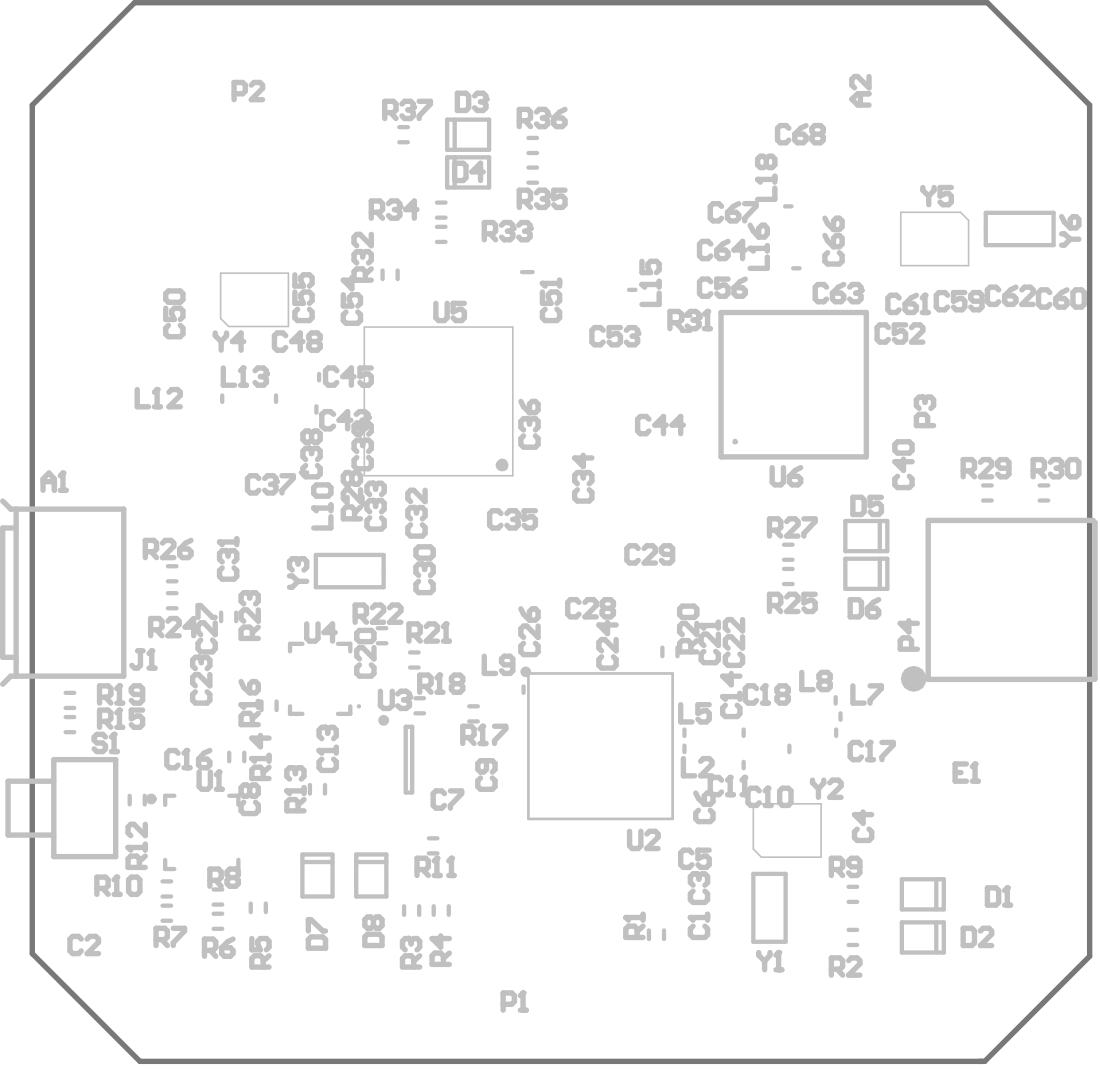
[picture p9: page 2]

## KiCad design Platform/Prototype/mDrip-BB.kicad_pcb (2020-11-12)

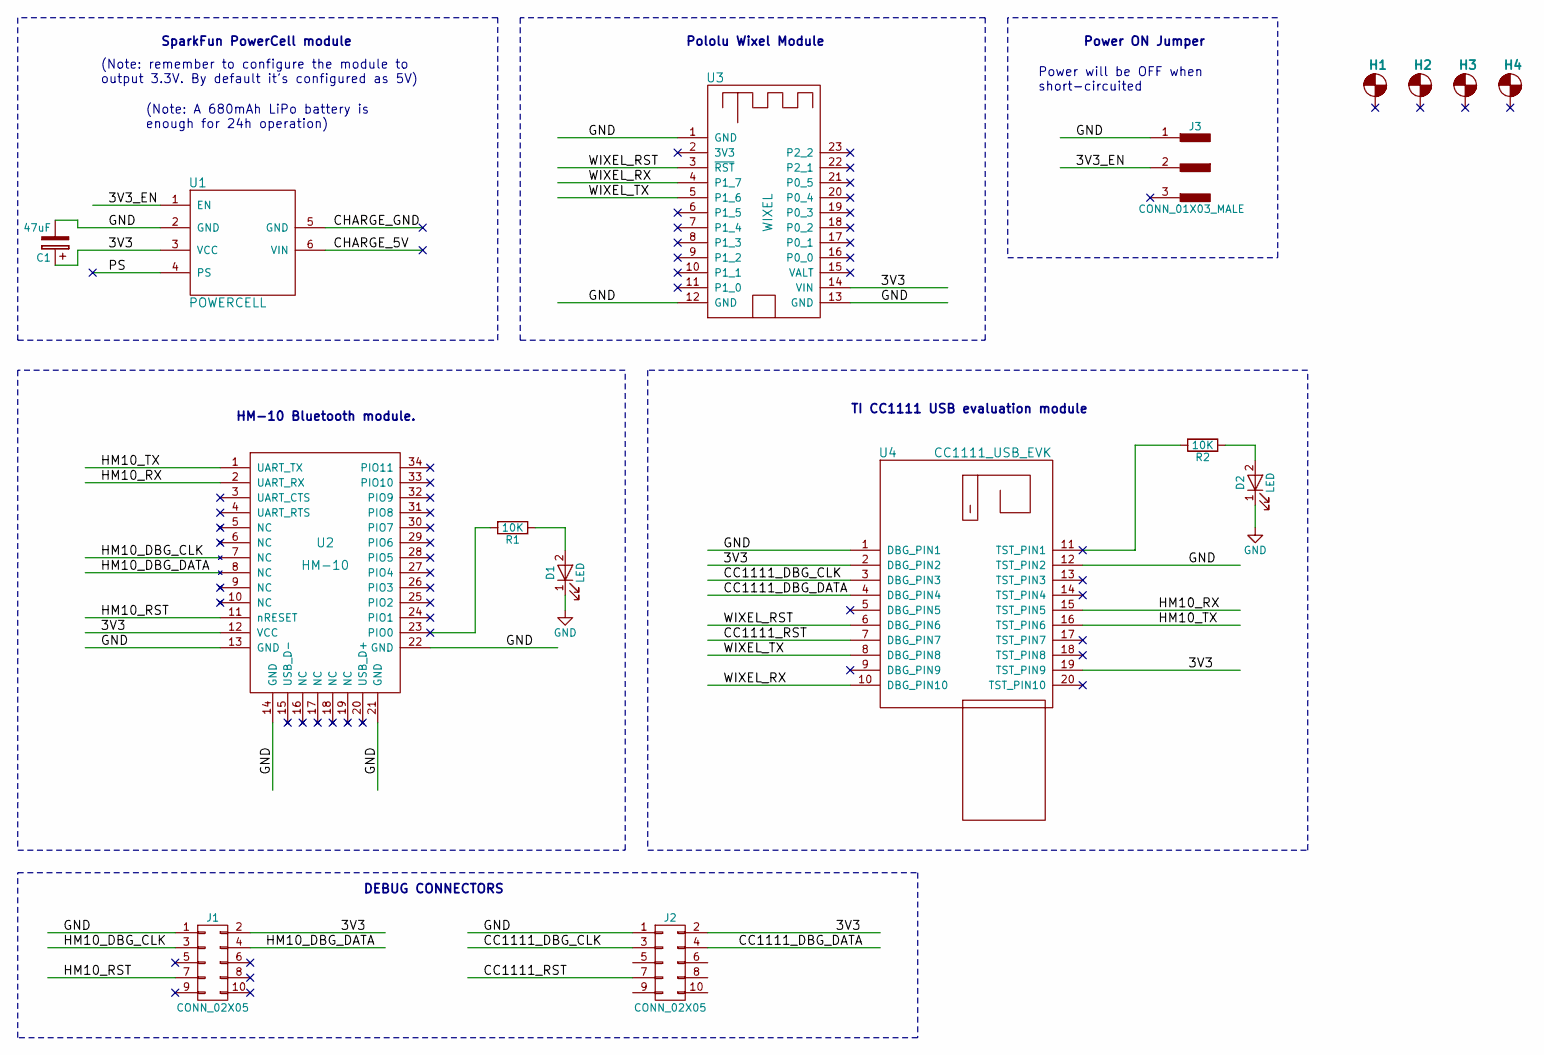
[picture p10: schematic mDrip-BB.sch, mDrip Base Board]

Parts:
C1: 47uF; CP_Radial_D5.0mm_P2.50mm
D1, D2: LED; LED_D5.0mm
H1, H2, H3, H4: Hole; MountingHole_2.7mm_M2.5_Pad
J1, J2: CONN_02X05; Pin_Header_Straight_2x05_Pitch2.54mm
J3: CONN_01X03_MALE; Pin_Header_Straight_1x03_Pitch2.54mm
R1, R2: 10K; R_Axial_DIN0204_L3.6mm_D1.6mm_P5.08mm_Horizontal
U1: POWERCELL
U2: HM-10; HM10; MPN HM-10
U3: WIXEL
U4: CC1111_USB_EVK

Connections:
/3V3: C1.1, J1.2, J2.2, U1.3 (VCC), U2.12 (VCC), U3.14 (VIN), U4.2 (DBG_PIN2), U4.19 (TST_PIN9)
/3V3_EN: J3.2, U1.1 (EN)
/CC1111_DBG_CLK: J2.3, U4.3 (DBG_PIN3)
/CC1111_DBG_DATA: J2.4, U4.4 (DBG_PIN4)
/CC1111_RST: J2.7, U4.7 (DBG_PIN7)
/CHARGE_5V: U1.6 (VIN)
/CHARGE_GND: U1.5 (GND)
/HM10_DBG_CLK: J1.3, U2.7 (NC)
/HM10_DBG_DATA: J1.4, U2.8 (NC)
/HM10_RST: J1.7, U2.11 (nRESET)
/HM10_RX: U2.2 (UART_RX), U4.15 (TST_PIN5)
/HM10_TX: U2.1 (UART_TX), U4.16 (TST_PIN6)
/PS: U1.4 (PS)
/WIXEL_RST: U3.3 (~RST), U4.6 (DBG_PIN6)
/WIXEL_RX: U3.4 (P1_7), U4.10 (DBG_PIN10)
/WIXEL_TX: U3.5 (P1_6), U4.8 (DBG_PIN8)
GND: C1.2, D1.1 (K), D2.1 (K), J1.1, J2.1, J3.1, U1.2 (GND), U2.13 (GND), U2.14 (GND), U2.21 (GND), U2.22 (GND), U3.1 (GND), U3.12 (GND), U3.13 (GND), U4.1 (DBG_PIN1), U4.12 (TST_PIN2)
unnamed: D1.2 (A), R1.1
unnamed: D2.2 (A), R2.1
unnamed: R1.2, U2.23 (PIO0)
unnamed: R2.2, U4.11 (TST_PIN1)

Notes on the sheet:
HM-10 Bluetooth module.
Power ON Jumper
Power will be OFF when short-circuited
SparkFun PowerCell module
(Note: remember to configure the module to output 3.3V. By default it's configured as 5V)
(Note: A 680mAh LiPo battery is enough for 24h operation)
DEBUG CONNECTORS
Pololu Wixel Module
TI CC1111 USB evaluation module

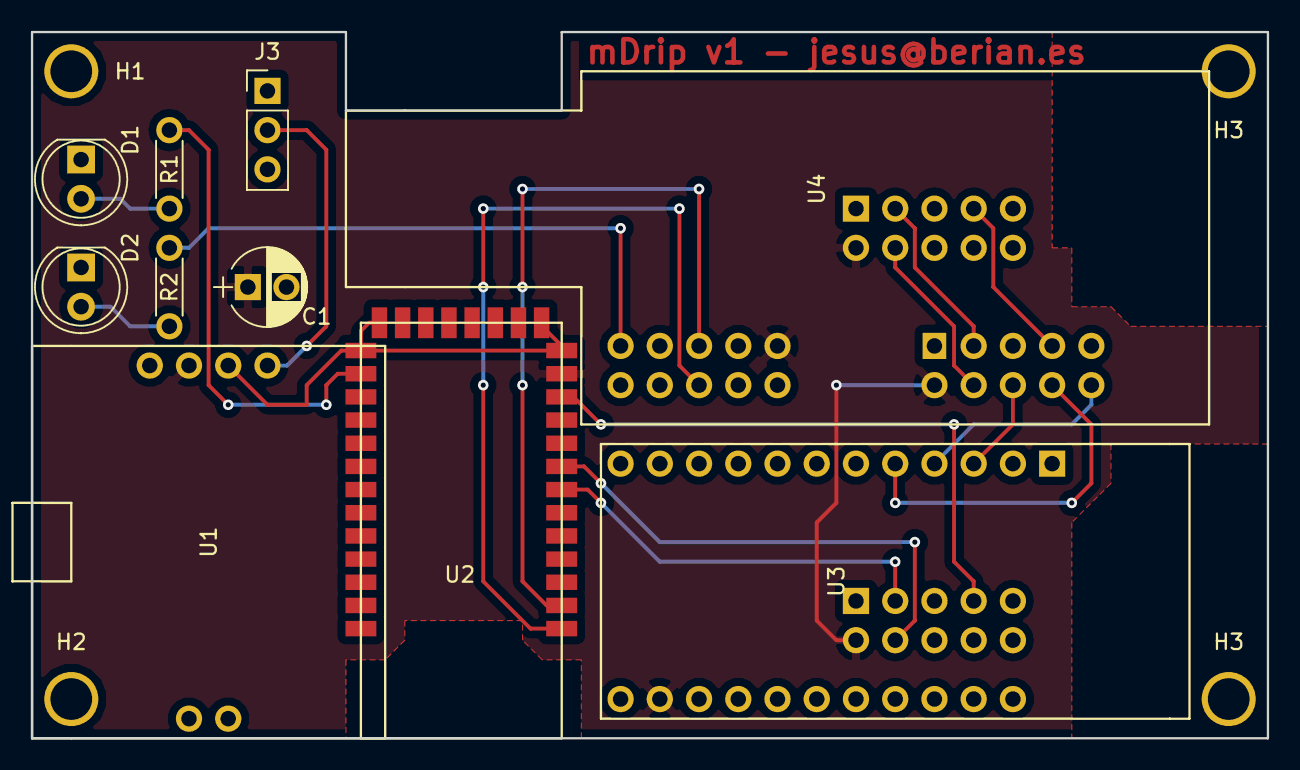
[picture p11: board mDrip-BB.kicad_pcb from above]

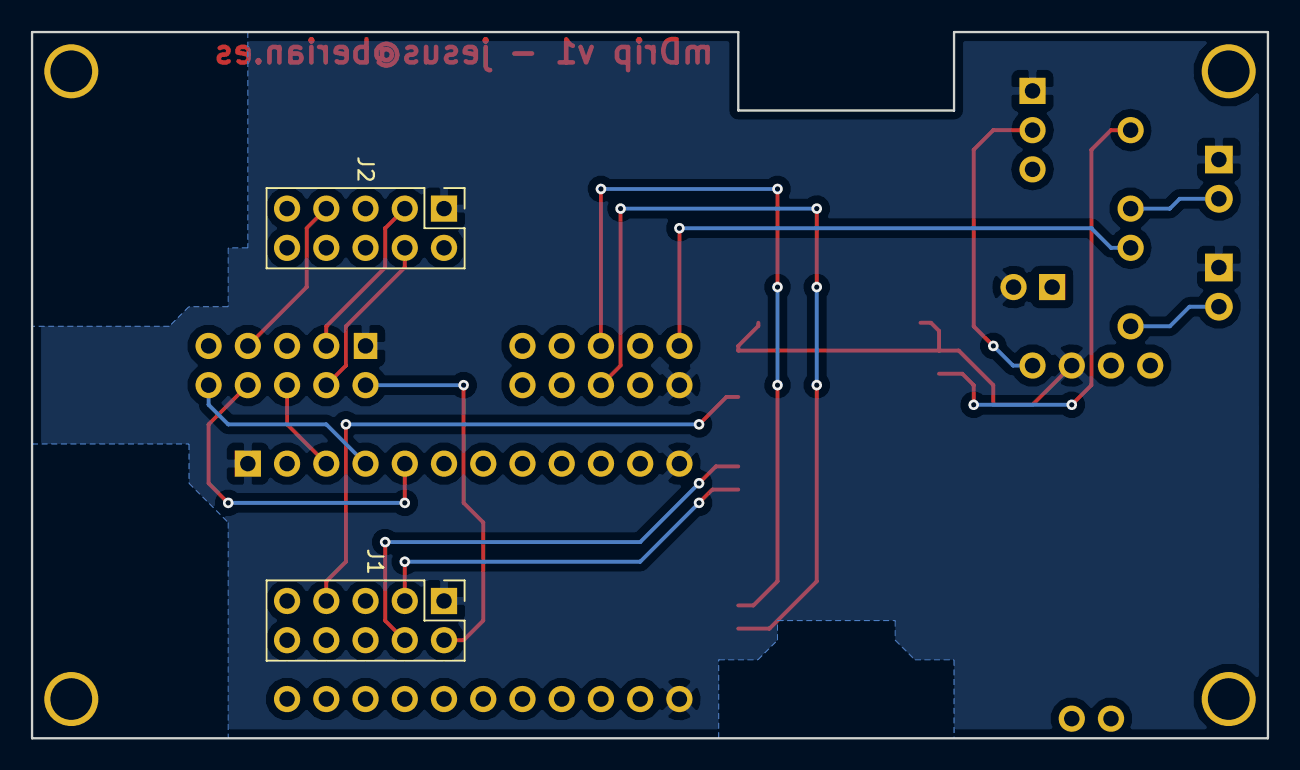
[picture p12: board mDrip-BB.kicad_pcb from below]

Board: 2 copper layers, 80.0 x 45.7 mm, 16 parts (2 on the bottom side), 18 nets.

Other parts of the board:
H3#2: MountingHole_2.7mm_M2.5_Pad

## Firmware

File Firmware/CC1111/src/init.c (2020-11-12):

#include "hal_types.h"
#include "hal_defs.h"
#include "hal_cc8051.h"
#include "ioCCxx10_bitdef.h"
#include "ioCC1110.h"
#include "constants.h"
#include "globals.h"
#include "init.h"
#include "freqManagement.h"

/***********************************************************************************
* LOCAL FUNCTIONS
*/
void configureIO (void)
{
    /* Set function of pin to general purpose I/O */
    P1SEL &= BIT0;
    P1SEL &= BIT1;
    P1SEL &= BIT5;
    P2SEL &= ~BIT0;

    /* Write value to pin. Note that this is a direct bit access.
     * Also note that the value is set before the pin is configured
     * as an output, as in some cases the value of the output needs
     * to be defined before the output is driven (e.g. to avoid
     * conflicts if the signal is shared with an other device)
     */
    P1_0 = 0;
    P1_1 = 0;
    GREEN_LED = 0;
    P1_5 = 0;

    /* Change direction to output */
    P2DIR |= BIT0;
    P1DIR |= BIT0;
    P1DIR |= BIT1;
    P1DIR |= BIT5;
}

void configureOsc (void)
{
  SLEEP &= ~OSC_PD_BIT;     // powering down all oscillators
  while(!XOSC_STABLE);      // waiting until the oscillator is stable
  asm("NOP");
  CLKCON &= 0xC0;
  CLKCON &= ~MAIN_OSC_BITS; // starting the Crystal Oscillator
  CLKCON |= 0x18;           // Tick speed = fref/8
  SLEEP |= OSC_PD_BIT;      // powering down the unused oscillator
  SLEEP &= ~0x80;           // Disable USB interface
}

void configureUART (void)
{

  /***************************************************************************
   * Setup I/O ports
   *
   * Port and pins used by USART0 operating in UART-mode are
   * RX     : P0_2
   * TX     : P0_3
   * CT/CTS : P0_4
   * RT/RTS : P0_5
   *
   * These pins can be set to function as peripheral I/O to be be used by UART0.
   * The TX pin on the transmitter must be connected to the RX pin on the receiver.
   * If enabling hardware flow control (U0UCR.FLOW = 1) the CT/CTS (Clear-To-Send)
   * on the transmitter must be connected to the RS/RTS (Ready-To-Send) pin on the
   * receiver.
   */

  // Configure USART0 for Alternative 1 => Port P0 (PERCFG.U0CFG = 0)
  // To avoid potential I/O conflict with USART1:
  // configure USART1 for Alternative 2 => Port P1 (PERCFG.U1CFG = 1)
  PERCFG = (PERCFG & ~PERCFG_U0CFG) | PERCFG_U1CFG;

  // Configure relevant Port P0 pins for peripheral function:
  // P0SEL.SELP0_2/3/4/5 = 1 => RX = P0_2, TX = P0_3, CT = P0_4, RT = P0_5
  P0SEL |= BIT5 | BIT4 | BIT3 | BIT2;

  /***************************************************************************
   * Configure UART
   *
   * The system clock source used is the HS XOSC at 48 MHz speed.
   */

  // Initialise bitrate = 9600 bbps (U0BAUD.BAUD_M = 163, U0GCR.BAUD_E = 7)
  U0BAUD = UART_BAUD_M;
  U0GCR = (U0GCR&~U0GCR_BAUD_E) | UART_BAUD_E;

  // Initialise UART protocol (start/stop bit, data bits, parity, etc.):

  // USART mode = UART (U0CSR.MODE = 1)
  U0CSR |= U0CSR_MODE;

  // Start bit level = low => Idle level = high  (U0UCR.START = 0)
  U0UCR &= ~U0UCR_START;

  // Stop bit level = high (U0UCR.STOP = 1)
  U0UCR |= U0UCR_STOP;

  // Number of stop bits = 1 (U0UCR.SPB = 0)
  U0UCR &= ~U0UCR_SPB;

  // Parity = disabled (U0UCR.PARITY = 0)
  U0UCR &= ~U0UCR_PARITY;

  // 9-bit data enable = 8 bits transfer (U0UCR.BIT9 = 0)
  U0UCR &= ~U0UCR_BIT9;

  // Level of bit 9 = 0 (U0UCR.D9 = 0), used when U0UCR.BIT9 = 1
  // Level of bit 9 = 1 (U0UCR.D9 = 1), used when U0UCR.BIT9 = 1
  // Parity = Even (U0UCR.D9 = 0), used when U0UCR.PARITY = 1
  // Parity = Odd (U0UCR.D9 = 1), used when U0UCR.PARITY = 1
  U0UCR &= ~U0UCR_D9;

  // Flow control = disabled (U0UCR.FLOW = 0)
  U0UCR &= ~U0UCR_FLOW;

  // Bit order = LSB first (U0GCR.ORDER = 0)
  U0GCR &= ~U0GCR_ORDER;
}

void initGlobals (void)
{
  int i,j;
  
  resetRequested = 0;
  bleTxIndexIn   = 0;
  bleTxIndexOut  = 0;
  bleRxIndexIn   = 0;
  bleRxIndexOut  = 0;
  bleTxing       = 0;
  bleRxFlag      = 0;
  timeCounter  = _MAX_TIMECOUNTER_VAL_;
  timeCounterOn  = 0;
  timeCounterOff = 0;
  timeCounterHoldProcess = 0;
  timeCounterBolusSnooze = 0;
  timeCounterBolusSnoozeEnable = 0;
  timeCounterPumpAwake = 0;
  timeCounterTxInhibit = 0;
  bleCommsWatchdogTimer = 0;
  mySentryFlag = 0;
  rfFrequencyMode = 0;
  timeUpdatedFlag = 0;
  sendFlag = 0;
  queryPumpFlag = 0;
  rfState[0] = 0;
  rfState[1] = 0;
  syncMode = 0;
  txTimer = 0;
  txing = 0;
  rfTXMode = 0;
  startRFTxFlag = 0;
  adjustSensitivityFlag = 0;
  lookForMySentryTimer = 0;
  lookForMinilinkTimer = 0;
  expectedSeqNum = 0;
  correctionTimeStamp = 0;
  glucoseDataSource = 0;
  tempBasalActiveRate = 0.0;
  tempBasalTimeLeft = 0;
  //bgUnits = BG_UNITS_NONE;
  //carbUnits = CARB_UNITS_NONE;

  lastMinilinkSeqNum = 0x80;
  for (i=0; i<3; i++) {
   minilinkID[i]     = 0x00;
   pumpID[i]         = 0x00;
   glucometerID[i]   = 0x00;
  }
  
  timingTableFrozen  = 0;
  timingTableCorrect = 0;
  for (i=0; i<8; i++) {
    missesTable[i] = 0x03;
    for (j=0; j<2; j++) {
      timingTable[i][j] = 0;
    }
  }
  
  /*for (i=0; i<MAX_NUM_BASALS; i++) {     
    pumpBasalsHour   [ i ] = 0;
    pumpBasalsMinute [ i ] = 0;
    pumpBasalsAmount [ i ] = 0;
  }*/
  pumpBasalsValidRanges = 0;
   
  /*for (i=0; i<MAX_NUM_INSULIN_SENS; i++) {     
    insulinSensHour   [ i ] = 0;
    insulinSensMinute [ i ] = 0;
    insulinSensAmount [ i ] = 0;
  }*/
  insulinSensValidRanges = 0;

  pumpTargetsValidRanges = 0;
  
  resetHistoryLogs();
  
  initFreqs();
  
  systemTimeHour         = 0;
  systemTimeMinute       = 0;
  systemTimeSecond       = 0;
  systemTimeSecondTimer  = 0;
  systemTimeSynced       = 0;
  
  //controlLoopMode = NO_CONTROL_LOOP;
  controlLoopAggressiveness = 2;
  controlLoopMaxTarget = 130;

  durationIOB = 3;
  //maxBolus    = 0;
  maxBasal    = 0;

  maxAbsorptionRate = 0.0;
  maxAbsorptionRateEnable = 0;

  initIOBRegisters();
  initResponseToInsulin((float)(durationIOB),30/5);
  //initResponseToInsulin(3.0,15/5);
  
  for (i=0; i<6; i++) {
    instantIOBHist[i] = 0.0;
    sgvDeriv[i] = 0;
    sensHist[i] = 0;
    basalHist[i] = 0;
  }
  numRes = 0;
  numHist = 0;
  basalHistNum = 0;
  
  measuredSensitivityValid  = 0;
  measuredBasalValid        = 0;
  
}

void initIOBRegisters (void)
{
  int i;
  
  basalVectorsInit = 0;
  for (i=0; i<MAX_NUM_IOB_REGISTERS; i++) {
    basalIOBvector    [i] = 0;
    bolusIOBvector    [i] = 0;
    responseToInsulin [i] = 0;
  }
  for (i=0; i<MAX_NUM_FUTURE_IOBS; i++) {
    basalIOBfuture    [i] = 0;
  }
  
  iobAccumBasal = 0.0;
  iobAccumBolus = 0.0;
}

void initResponseToInsulin (float hours, char offset)
{
  float idx;
  float tempValue;
  int idxInit, idxEnd;
  int i;
  int32 normSum;
  //char offset;
  
  //offset = 2; // 10 min / 5 min = 2
  
  if (hours > 8.0) hours = 8.0;
  else if (hours < 0.0) hours = 0.0;
  
  // Curve calculation
  // 
  //    Humalog Response
  //    https://dailymed.nlm.nih.gov/dailymed/archives/image.cfm?archiveid=41365&type=img&name=humalog-f001-v1.jpg
  //
  idxInit = 0;
  idx = (0.0*hours/3.0)/5.0 + offset;
  idxEnd  = (int)idx;
  for (i=idxInit;i<=idxEnd;i++) {
    if ((i>=0) && (i<MAX_NUM_IOB_REGISTERS)) {
      tempValue = 0.0*((float)(i) / (float)(idxEnd));
      responseToInsulin[i] = (unsigned int) (tempValue*16380.0);
    }
  }
  idxInit = idxEnd;
  idx = (25.0*hours/3.0)/5.0  + offset;
  idxEnd  = (int)idx;
  for (i=idxInit;i<=idxEnd;i++) {
    if ((i>=0) && (i<MAX_NUM_IOB_REGISTERS)) {
      tempValue = 0.477*((float)(i) / (float)(idxEnd));
      responseToInsulin[i] = (unsigned int) (tempValue*16380.0);
    }
  }
  idxInit = idxEnd;
  idx = (45.0*hours/3.0)/5.0  + offset;
  idxEnd  = (int)idx;
  for (i=idxInit;i<=idxEnd;i++) {
    if ((i>=0) && (i<MAX_NUM_IOB_REGISTERS)) {
      tempValue = 0.477 + (0.9-0.477)*((float)(i-idxInit)/(float)(idxEnd-idxInit));
      responseToInsulin[i] = (unsigned int) (tempValue*16380.0);
    }
  }
  idxInit = idxEnd;
  idx = (60.0*hours/3.0)/5.0  + offset;
  idxEnd  = (int)idx;
  for (i=idxInit;i<=idxEnd;i++) {
    if ((i>=0) && (i<MAX_NUM_IOB_REGISTERS)) {
      tempValue = 0.9 + (0.99-0.9)*((float)(i-idxInit)/(float)(idxEnd-idxInit));
      responseToInsulin[i] = (unsigned int) (tempValue*16380.0);
    }
  }  
  idxInit = idxEnd;
  idx = (150.0*hours/3.0)/5.0 + offset;
  idxEnd  = (int)idx;
  for (i=idxInit;i<=idxEnd;i++) {
    if ((i>=0) && (i<MAX_NUM_IOB_REGISTERS)) {
      tempValue = 0.99 - (0.99-0.5)*((float)(i-idxInit)/(float)(idxEnd-idxInit));
      responseToInsulin[i] = (unsigned int) (tempValue*16380.0);
    }
  }  
  idxInit = idxEnd;
  idx = (210.0*hours/3.0)/5.0 + offset;
  idxEnd  = (int)idx;
  for (i=idxInit;i<=idxEnd;i++) {
    if ((i>=0) && (i<MAX_NUM_IOB_REGISTERS)) {
      tempValue = 0.5 - (0.5-0.2)*((float)(i-idxInit)/(float)(idxEnd-idxInit));
      responseToInsulin[i] = (unsigned int) (tempValue*16380.0);
    }
  } 
  idxInit = idxEnd;
  idx = (420.0*hours/3.0)/5.0 + offset;
  idxEnd  = (int)idx;
  for (i=idxInit;i<=idxEnd;i++) {
    if ((i>=0) && (i<MAX_NUM_IOB_REGISTERS)) {
      tempValue = 0.2 - (0.2-0.05)*((float)(i-idxInit)/(float)(idxEnd-idxInit));
      responseToInsulin[i] = (unsigned int) (tempValue*16380.0);
    }
  } 
  idxInit = idxEnd;
  idx = (440.0*hours/3.0)/5.0 + offset;
  idxEnd  = (int)idx;
  for (i=idxInit;i<=idxEnd;i++) {
    if ((i>=0) && (i<MAX_NUM_IOB_REGISTERS)) {
      tempValue = 0.05 - (0.05-0.01)*((float)(i-idxInit)/(float)(idxEnd-idxInit));
      responseToInsulin[i] = (unsigned int) (tempValue*16380.0);
    }
  }   
  idxInit = idxEnd;
  idx = (480.0*hours/3.0)/5.0 + offset;
  idxEnd  = (int)idx;
  for (i=idxInit;i<=idxEnd;i++) {
    if ((i>=0) && (i<MAX_NUM_IOB_REGISTERS)) {
      tempValue = 0.01 - 0.01*((float)(i-idxInit)/(float)(idxEnd-idxInit));
      responseToInsulin[i] = (unsigned int) (tempValue*16380.0);
    }
  }   
  
  // Normalization
  normSum = 0;
  for (i=0; i<MAX_NUM_IOB_REGISTERS; i++) normSum += responseToInsulin[i];
  tempValue = (float)(normSum) / 16382.0;
  for (i=0; i<MAX_NUM_IOB_REGISTERS; i++) {
    responseToInsulin[i] = (unsigned int)((float)(responseToInsulin[i])/tempValue); 
  }
}

void resetHistoryLogs (void)
{
  char i;
  
  for (i=0; i<16; i++) {
    historySgv         [i] = 0;
    historyRawSgv      [i] = 0;
    historyRaw         [i] = 0;
    historySgvValid    [i] = 0;
    historyRawSgvValid [i] = 0;
    historyRawValid    [i] = 0;
  }
}

void initFreqs (void)
{
  int i = 0;
  if (rfFrequencyMode == 0 ) {
    genericFreq[2]    = 0x24;
    genericFreq[1]    = 0x2E;             // f = 868.4 MHz
    genericFreq[0]    = 0xC0; //0x38
    genericBW         = _WIDE_BANDWIDTH_;
  } else {
    genericFreq[2]    = 0x26;
    genericFreq[1]    = 0x30;             // f = 916.5 MHz
    genericFreq[0]    = 0x70;
    genericBW         = _WIDE_BANDWIDTH_; 
  }
  
  minilinkBW          = genericBW;
  pumpBW              = genericBW;
  glucometerBW        = genericBW;
  
  for (i=0; i<32; i++) {
    minilinkRSSI   [ i ] = 0x00 ;
    pumpRSSI       [ i ] = 0x00 ;
    glucometerRSSI [ i ] = 0x00 ;
  }
  
  minilinkRSSI   [ 32 ] = 0x01 ;
  pumpRSSI       [ 32 ] = 0x01 ;
  glucometerRSSI [ 32 ] = 0x01 ;
  
  lastMinilinkChannel   = 0 ;
  lastPumpChannel       = 0 ;
  lastGlucometerChannel = 0 ;
  
  bestMinilinkFreqFound   = 0 ;
  bestPumpFreqFound       = 0 ;
  bestGlucometerFreqFound = 0 ;
}

void reset (void)
{
 // (*((void (* __code *)(void))0))(); // Reset
 EA = 0;  // Disable global interrupt 
 WDCTL = 0xA0;
 WDCTL = 0x50; // Clear timer
 WDCTL = 0x8B; // Enable watchdog to force reset
}

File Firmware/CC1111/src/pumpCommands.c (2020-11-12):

#include "constants.h"
#include "globals.h"
#include "crc_4b6b.h"
#include "medtronicRF.h"
#include "init.h"
#include "pumpCommands.h"
#include "freqManagement.h"
#include "bleComms.h"
#include "dataProcessing.h"

#define QUEUE_SLOTS           2
#define QUEUE_MAX_MSG_SIZE   80
#define DEFAULT_MSG_TIMEOUT  ((0*60 + 8)*TICKS_PER_SECOND)
#define DEFAULT_MSG_RETRIES   3

unsigned char __xdata pumpCmdQueuePendingNumber                                    ;
unsigned char __xdata pumpCmdQueuePending   [ QUEUE_SLOTS ]                        ;
         char __xdata pumpCmdQueueMsg       [ QUEUE_SLOTS ] [ QUEUE_MAX_MSG_SIZE ] ;
         char __xdata pumpCmdQueueExpectAns [ QUEUE_SLOTS ]                        ;
unsigned int  __xdata pumpCmdQueueLen       [ QUEUE_SLOTS ]                        ;
         int  __xdata pumpCmdQueueTimes     [ QUEUE_SLOTS ]                        ;
unsigned long __xdata pumpCmdQueueTimeout   [ QUEUE_SLOTS ]                        ;
unsigned char __xdata pumpCmdQueueRetries   [ QUEUE_SLOTS ]                        ;

unsigned char numberOfPendingMsgs (void)
{
  char i;
  char pending = 0;
  
  for (i=0; i<QUEUE_SLOTS; i++) if (pumpCmdQueuePending[i] == 1) pending++;
  
  return(pending);
}

char addMsgToQueue (char *msg, unsigned int length, int times, char expectedAnswer, 
                    unsigned long timeout, unsigned char retries)
{
  int i;
  char slot;
  
  // Look for empty slot
  slot = QUEUE_SLOTS;
  for (i=QUEUE_SLOTS-1; i>=0; i--) 
    if (pumpCmdQueuePending[i] == 0) slot = i;
  
  // Check if the message fits
  if (length > QUEUE_MAX_MSG_SIZE) return(-1);
  
  // If a slot is available, add the message to the queue
  if (slot < QUEUE_SLOTS) {
    for (i=0; i<length; i++) pumpCmdQueueMsg[slot][i] = msg[i];
    pumpCmdQueueTimes[slot]     = times;
    pumpCmdQueueLen[slot]       = length;
    pumpCmdQueueTimeout[slot]   = timeout;
    pumpCmdQueueRetries[slot]   = retries;
    pumpCmdQueueExpectAns[slot] = expectedAnswer;
    pumpCmdQueuePending[slot]   = 1;
  } else {
    // Return error if no slot was found
    return(-1);
  }
  
  pumpCmdQueuePendingNumber = numberOfPendingMsgs ();
  
  return(slot);
}

void removeMsgFromQueue (char slot)
{
  char i,j;
  
  for (i=slot; i<QUEUE_SLOTS-1; i++) {
    if (pumpCmdQueuePending[i+1] == 1) {
      pumpCmdQueueTimeout[i]   = pumpCmdQueueTimeout[i+1];
      pumpCmdQueueRetries[i]   = pumpCmdQueueRetries[i+1];
      pumpCmdQueueTimes[i]     = pumpCmdQueueTimes[i+1];
      pumpCmdQueueLen[i]       = pumpCmdQueueLen[i+1];
      for (j=0; j<pumpCmdQueueLen[i+1] && j<QUEUE_MAX_MSG_SIZE; j++) 
        pumpCmdQueueMsg[i][j]  = pumpCmdQueueMsg[i+1][j];
      pumpCmdQueueExpectAns[i] = pumpCmdQueueExpectAns[i+1];
      pumpCmdQueuePending[i]   = 1;
    } else {
      pumpCmdQueueTimeout[i]   = 0;
      pumpCmdQueueRetries[i]   = 0;
      pumpCmdQueueTimes[i]     = 0;
      pumpCmdQueueLen[i]       = 0;
      pumpCmdQueuePending[i]   = 0;
      pumpCmdQueueExpectAns[i] = 0;
    }
  }
  
  pumpCmdQueueTimeout  [QUEUE_SLOTS-1] = 0;
  pumpCmdQueueRetries  [QUEUE_SLOTS-1] = 0;
  pumpCmdQueueTimes    [QUEUE_SLOTS-1] = 0;
  pumpCmdQueueLen      [QUEUE_SLOTS-1] = 0;
  pumpCmdQueuePending  [QUEUE_SLOTS-1] = 0;
  pumpCmdQueueExpectAns[QUEUE_SLOTS-1] = 0;
  
  pumpCmdQueuePendingNumber = numberOfPendingMsgs ();
  
}
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
